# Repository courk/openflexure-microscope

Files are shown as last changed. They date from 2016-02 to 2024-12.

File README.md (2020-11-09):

# OpenFlexure Microscope
The OpenFlexure Microscope is a  3D printable microscope, including a precise mechanical stage to move the sample and focus the optics.  There are many different options for the optics, ranging from a webcam lens to a 100x, oil immersion objective.

A trio of microscopes

The trick of making a microscope out of a webcam has been around for a little while, and produces good results.  However, getting a nice mechanical stage to focus the microscope and move around on the sample is tricky.  This project is a 3D printable design that enables very fine (sub-micron) mechanical positioning of the sample and the lens, with surprisingly good mechanical stability.  It's discussed in various [media articles](https://gitlab.com/openflexure/openflexure-microscope/wikis/Media-Articles).

If you use the OpenFlexure microscope in you work please consider citing one of our papers:

* *Robotic microscopy for everyone: the OpenFlexure microscope*, [Biomedical Optics Express **11** 2447 (2020)](https://doi.org/10.1364/BOE.385729) (open access).
* *A one-piece 3D printed flexure translation stage for open-source microscopy*, [Review of Scientific Instruments **87**, 025104 (2016)](http://dx.doi.org/10.1063/1.4941068) (open access).

## Building a microscope
For up-to-date build instructions, STL files, and pre-built Raspberry Pi SD images, please head to the [build a microscope page].

[build a microscope page]: https://openflexure.org/projects/microscope/build

## Instructions
The latest release of our assembly documentation can be found from the [build a microscope page] on our website. The editable instructions are Markdown format, in the [docs folder](./docs/) of this repository. If you have a problem accessing the images after cloning the repository see the section on LFS files below.

## Printing it yourself
Configure your microscope hardware and download the STL files through the [microscope STL configurator] page.  The [assembly instructions](https://build.openflexure.org/openflexure-microscope/latest/docs) contain instructions on print settings and putting it together.

If you've built one, let us know. You can let us know on [our forum](https://openflexure.discourse.group/), add yourself to the [wiki page of builds](https://gitlab.com/openflexure/openflexure-microscope/wikis/Assembly-Logs), or submit an [issue](https://gitlab.com/openflexure/openflexure-microscope/issues/new) marked as a build report.  This is a really helpful for us even if you don't suggest improvements or flag up problems.

[microscope STL configurator]: https://microscope-stls.openflexure.org

## Come join us!
Most of the development of this design has been done as part of various [research projects](http://www.bath.ac.uk/physics/contacts/academics/richard-bowman/index.html) - if you would like to join our research group at Bath, and you have funding or are interested in applying for it, do get in touch.  Check the University of Bath jobs site, or findaphd.com, to see if we are currently advertising any vacancies.  The team is bigger than Bath, though, and there are contributors in Cambridge, Dar es Salaam, and beyond.

## Kits and License
This project is open-source and is released under the CERN open hardware license.  We are working on bring able to sell kits through [OpenFlexure Industries Ltd.](https://www.openflexure.com/), and will update here once we have a good way of doing it.

## Get Involved!
This project is open so that anyone can get involved, and you don't have to learn OpenSCAD to help (although that would be great).  Ways you can contribute include:

* [Join our forum](https://openflexure.discourse.group/)
* Get involved in [discussions on gitter] (we use this less than the forum)(https://gitter.im/OpenFlexure-Microscope/Lobby) 
* Share your microscope images (of both microscopes and what you've seen with them) on social media - you can mention @openflexure on Twitter.
* [Raise an issue on the helpdesk](https://gitlab.com/openflexure/openflexure-helpdesk/-/issues) if you spot something that's wrong, or something that could be improved.  Helpdesk issues can be about anything to do with the project including the instructions/documentation, the software, etc.
* Suggest better text or images for the instructions.
* Improve the design of parts - even if you don't use OpenSCAD, STL files or descriptions of changes are helpful.
* Fork it, and make merge requests - again, documentation improvements are every bit as useful as revised OpenSCAD files.

Things in need of attention are currently described in [issues](https://gitlab.com/openflexure/openflexure-microscope/issues/) so have a look there if you'd like to work on something but aren't sure what.

## Developing
If you want to play with the OpenSCAD files or change the documentation, you should fork the repository.  You can edit the documentation online in GitLab, or clone the repository if you want to edit the OpenSCAD files.  You will need to clone the whole repository as the OpenSCAD files are dependent on each other.

### Development environment
We mostly use VSCode to edit the OpenSCAD files, and then use OpenSCAD with the editor hidden and the "automatic reload and compile" option ticked.  This is much nicer for a big multi-file project like the microscope than relying on OpenSCAD's built-in editor, and also works nicely with version control.

You can edit ``microscope_parameters.scad`` to change which options you build in the OpenSCAD window, but it's best not to commit changes to that file unless you need to change the default values.

### Automatic builds
The build system is based on Python and Ninja, see [compiling](COMPILE.md) for more details.

### Release flow
We use GitLab CI to manage builds and deployment.

The CI will build STL files that will remain on GitLab for 1 week when:

* A merge request is submitted
* A merge request is modified

The CI will build and deploy STL files and documentation to [build.openflexure.org](https://build.openflexure.org/) when:
* A build is manually triggered from GitLab web
* A release is tagged

The build server will mark a release as "latest" ([build.openflexure.org/openflexure-microscope/latest](https://build.openflexure.org/openflexure-microscope/latest)) when a release is tagged, with a full semantic version and no suffix. For example:
  * v6.0.0 will replace "latest"

However, incomplete semantic versions will not replace latest. For example:
  * v6.0.1-beta.1 will **not** replace "latest" (pre-release suffix)
  * v6.1 will **not** replace "latest" (no patch version specified)
  * 6.0.1a will **not** replace "latest" (non-standard suffix)

### LFS files

This repository stores images using Git LFS. This means that cloning the repository without Git LFS installed will only download placeholders for the images. Follow these instructions to [install Git LFS](https://git-lfs.github.com/).

With LFS installed Git will download the latest version of the images used in the documentation. If they are still missing try running:
```
git lfs fetch
git lfs checkout
```

**Download all files**

To make Git always download *everything* in the repository run the following commands in your terminal:
```
git config --local lfs.fetchexclude ""
git lfs fetch
git lfs checkout
```

## Related Repositories

Other repositories relating to the Openflexure Microscope are in the [OpenFlexure GitLab group](https://gitlab.com/openflexure).  Particularly useful ones are:

* [OpenFlexure Microscope Server](https://gitlab.com/openflexure/openflexure-microscope-server). This is the software that runs on the microscope.
* [OpenFlexure Connect](https://gitlab.com/openflexure/openflexure-connect). The recommended client software for controlling the microscope. The repository is mostly device discovery code, with the interface handled by the server.
* [OpenFlexure Microscope Python Client](https://gitlab.com/openflexure/openflexure-microscope-pyclient). This allows you to control a microscope from a python script.
* [OpenFlexure Delta Stage](https://gitlab.com/openflexure/openflexure-delta-stage). A 3-axis stage for microscopy that keeps the objective in a fixed position.
* [OpenFlexure Block Stage](https://gitlab.com/openflexure/openflexure-block-stage). A higher precision 3-axis stage with a smaller range.

Repositories for compatible motor controllers:
* The ["sangaboard" motor controller](https://gitlab.com/bath_open_instrumentation_group/sangaboard). The standard motor controller for the microscope. Developed collaboratively with [STICLab](http://www.sticlab.co.tz)
* The ["fergboard" motor controller](https://github.com/fr293/motor_board) by Fergus Riche.

A number of other related projects include:

* [micat](https://gitlab.com/bath_open_instrumentation_group/micat) For microscope calibration
* [PiCamera CRA Compensation](https://gitlab.com/bath_open_instrumentation_group/picamera_cra_compensation/) Contains hardware and software for colour calibration of a Raspberry Pi camera.
* Some [characterisation scripts for analysing images of the USAF resolution test target](https://github.com/rwb27/usaf_analysis/)

Some open flexure repositories still remain on [Richard's Github](https://github.com/rwb27/).

## Compiling from source
If you want to print the current development version, you can compile the STL from the OpenSCAD files - but please still consult the documentation for quantities and tips on print settings, etc.  You can use Ninja build to generate all the STL files (run ``pip3 install -r requirements.txt`` and then ``./build.py`` in the root directory of the repository).  More instructions are available in [COMPILE.md](COMPILE.md).

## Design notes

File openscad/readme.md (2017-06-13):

OpenFlexure Microscope: OpenSCAD Source
=======================================

This folder contains the source code that generates the STL files that you print to produce the microscope.  The relationship between the source files and the STL files is not yet 1:1, though I'm gradually working on that.  Most of the SCAD files produce a corresponding STL, but there are a few key support files that don't:

* ``microscope_parameters.scad`` defines most of the important variables (parameters) used in the design, for example the size of the microscope, whether or not it has motor lugs, etc. etc. - this is the file you are most likely to need to modify, for example to produce a microscope with particular settings.
* ``utilities.scad`` contains lots of handy functions I've coded along the way.  It's a slightly random assortment, but they are used in most of the other files and save a fair bit of typing.
* ``dovetail.scad`` defines the dovetail clips used to hold the optics module and the condenser.
* ``compact_nut_seat.scad`` defines the actuator column (the bit that holds the screw, nut and elastic band).  This is one of the most useful files for other projects - e.g. the OpenFlexure Block Stage uses it extensively.
* ``logo.scad`` is used to stamp the WaterScope logo on the microscope

Then for the main parts of the microscope:
* ``main_body.scad`` defines the main body.  This is by far the biggest file as you might expect.
* ``feet.scad`` produces the three front feet (two tilted and one untilted)
* ``gears.scad`` makes 3 gears for the actuators.
* ``illumination_and_rear_foot.scad`` produces the illumination column, which is combined with the back foot.  It's now in three pieces, for easier printing and to allow some adjustment of the condenser position.
* ``optics.scad`` defines, amongst other things, the optics module (the mount for the camera and objective).  This has a number of commented-out sections that must be uncommented depending on what you want to produce.  In particular, you must choose manually between an RMS objective and using a simpler lens.  You must also uncomment the correct line at the top of the file for the camera - the design will work with several camera modules defined in the ``cameras`` folder.
* ``sample_clip_2.scad`` produces clips to hold microscope slides onto the microscope stage.  This is now set to print two, and produces an STL file that is print-ready (i.e. the clips are on their side).
* ``sample_riser_2.scad`` makes a 10mm thick platform for a microscope slide.  You may need to use comments at the bottom of the file to print either the sample riser or the clip that holds the slide on.  A small spring is required to put the clip in the right place.
* ``small_gear.scad`` makes the gear you fit on a motor if you want to motorise the microscope.  NB it only makes one gear.

There are some that make tools too:
* ``actuator_assembly_tools.scad`` defines the tool for inserting elastic bands, and the tooll for pushing nuts into nut slots.  NB there is a new double-ended band tool defined at the bottom of the file, you'll need to use the comments to either produce this or the old-style one.
* ``tube_lens_tool.scad`` produces a ring of plastic, suitable for pushing the tube lens into its push-fit mount without damaging it.
* ``condenser_lens_tool.scad`` produces a ring of plastic, suitable for pushing the condenser lens into its push-fit mount without damaging it.
* ``lens_removal_tools.scad`` produces the tools needed to remove the lens from the Raspberry Pi camera module.  NB the lens removal tool is now superseded by the injection-moulded tool supplied by Raspberry Pi with each camera, but the board holder still helps to avoid damaging the flex.

Other files:
* ``baseplate.scad`` and ``baseplate_minimal.scad`` generate a baseplate, suitable for gluing onto some foam, if you want to mount the microscope in a box.  It's still work in progress...
* ``illustrations/`` contains various SCAD files that aim to create the illustrations needed for the instructions.  Very much work in progress, it's nowhere near finished.

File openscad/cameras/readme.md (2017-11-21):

# OpenFlexure Microscope: Camera Mounts

Curently, the OpenFlexure microscope will work with:
* Raspberry Pi camera module v2 (v1 is possible but deprecated, as it's discontinued)
* Logitech C270 webcam (you need to dissassemble it and remove the microphone)
* USB camera with standard M12 lens (WaterScope source these from China)

The way this is done is that ``optics.scad`` includes ``camera.scad``, which defines the important functions/modules for interfacing with the camera.  These are then used to make the optics module accordingly.  The variable ``camera`` (defined in ``microscope_parameters.scad`` or on the command line). Those functions are:

* ``camera_mount_height()``: a function that returns the height of the mount (above this height, we will make the optics module - this is the distance below the ground plane of the microscope body that the camera PCB will sit).
* ``camera_sensor_height()``: the distance above the PCB that the camera sensor sits - it's used in the optics module to calculate the position of the lens.
* ``camera_mount()``: a module that builds a mount for the camera.  If you print this on its own, it should create a flat(ish) structure, ``camera_mount_height()`` high, that fits onto the camera, with the sensor centred on the origin.

There are 3 options for the camera:
* picamera_2: mount for Raspberry Pi camera v2
* logitech_c270: for Logitech C270 webcam
* m12: this replaces the M12 lens holder on a USB camera.  It should work with most cameras that have an M12 lens held onto the board by two screws.

The ``picamera_2.scad`` file also defines the cover for the bottom of the camera PCB and the tools for removing the lens (see below).  There's no cover for the Logitech PCB, I often use a bit of extra-large heatshrink (it's thinner than a printed cover would be, which is helpful).

Previous versions of the microscope had push-fit mounts for the Pi camera v1 and v2, but it was very easy to break the delicate flex on the camera module when fitting these, so they are now removed.  See previous versions if you need those.

## Pi Camera v2 accessories
The extra files ``picamera_2_<thing>.scad`` generate the board gripper and lens gripper that can be used to remove the lens of the Raspberry Pi camera v2, and a little cover for the bottom of the PCB to protect it from shorts, etc.  The lens gripper is now obsolete as a much better, injection-moulded gripper is now supplied in the pi camera box.  The gripper for the PCB is still useful as it protects the flex cable from damage while you remove the lens.

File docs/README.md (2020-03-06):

# OpenFlexure Microscope Documentation
The documentation is best viewed [on openflexure.org][built_docs].  If you have problems or want to suggest improvements, please [raise an issue] or even better edit the markdown file in this folder and send us a pull request.

The assembly instructions are contained in this folder, in MarkDown format.  They will eventually use [Git-Building] to automatically generate the bill of materials, which means the markdown files will make sense if you view them directly, but you're better off using the [processed versions][built_docs] on openflexure.org.

## Improving the documentation
If you would like to improve the documentation, the easiest way is to use the "edit" or "web IDE" features on GitLab.  Good instructions are super important, so it's really helpful to have suggestions and improvements from people who have built the microscope.  You can fork the repository and work on it locally if you prefer.  

**Please note that this repository uses [Git LFS] and that, by default, it won't download the images for the documentation** (before switching to LFS, it was a 1.5Gb download to clone the repository, which causes real problems for some of the team).  To change which files Git LFS downloads please see the instructions in the main [README](../README.md) for the repository.

## Build instructions
Currently, the process of getting the docs onto [openflexure.org][built_docs] is a bit manual; first you need to add Jekyll "front matter" to the pages and copy them into a new location.  That's done by ``build_docs.py`` (in this directory - use Python 3 or it won't work).  You can then copy all the files from the built directory (``../builds/docs/`` by default) into the relevant folder in the repoisitory for openflexure.gitlab.io, and push to master at which point the Jekyll site will be built.  We will hopefully switch to using gitbuilding in the near future to improve this and automate our bill of materials generation.  You can of course serve the output folder as a Jekyll site directly if you add a config file, but bear in mind that it might get deleted when you rebuild the output folder, so keep a copy somewhere else!  This will be fixed in the future when we are using gitbuilding.

[built_docs]: https://www.openflexure.org/projects/microscope/docs/
[Git LFS]: https://git-lfs.github.com/
[Git-Building]: https://gitlab.com/bath_open_instrumentation_group/git-building
[raise an issue]: https://gitlab.com/openflexure/openflexure-microscope/issues/new

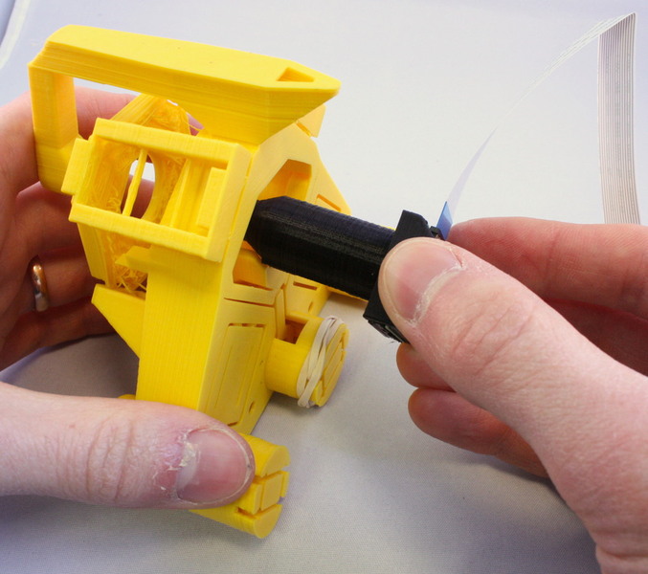
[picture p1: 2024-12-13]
docs/images/optics_insertion_1.jpg

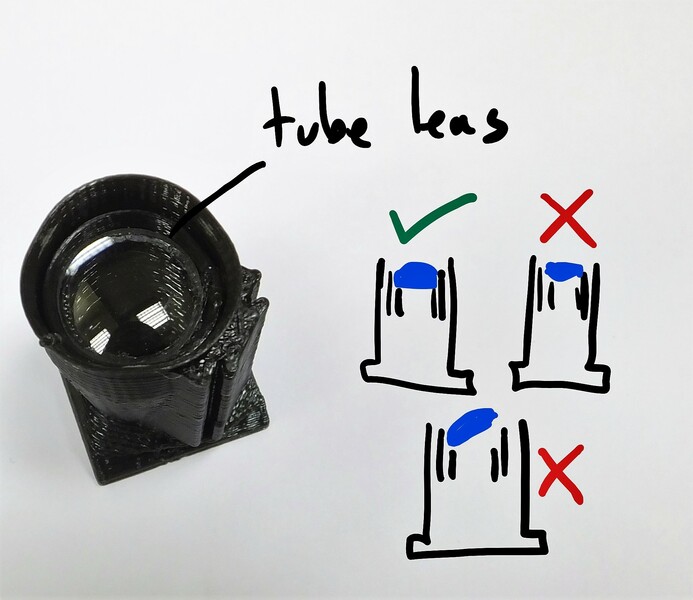
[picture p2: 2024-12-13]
docs/images/hires_optics_tubelens_2.jpg

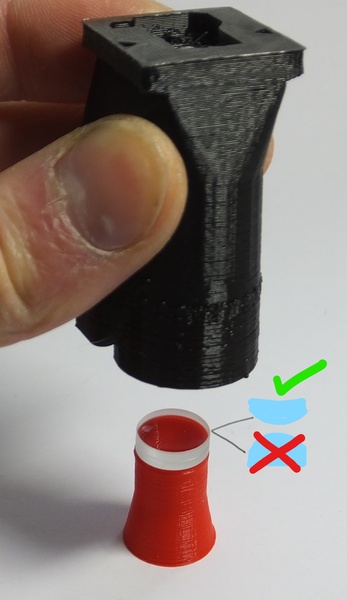
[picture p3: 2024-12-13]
docs/images/hires_optics_tube_lens_1.jpg

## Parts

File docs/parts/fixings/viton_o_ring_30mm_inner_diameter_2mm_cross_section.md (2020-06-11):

# Viton O ring, 30mm inner diameter, 2mm cross section

## Details
*   **Material:** Viton or Nitrile
*   **Inner diameter:** 30mm
*   **Cross-section:** 2mm
*   **Outer diameter:** 34mm
*   **Supplier website:** [http://www.simplybearings.co.uk/]

The O-rings function as springs, to provide a return force on the nut that is pulled upwards by the screw.  I use Viton O-rings, 30mm ID, as they provide about the right force.  You can substitute for rubber bands, but it's difficult to specify the size directly, and they tend to perish and snap in a few weeks.  Viton O rings are well worth the effort and price!

## Alternatives
If you're unable to get hold of Viton O rings of the correct size, substituting for Nitrile or EPDM is probably also fine - though most of our testing has been done with Viton.  

Rubber bands from a stationary store can work, though in our experience they usually perish after a few weeks.  Unfortunately, that happens whether or not they are used.  It's also usually quite hard to get rubber bands exactly the right size.

It's possible to print elastic bands using TPU filament, as described in Bill Schaller's contribution.  Print this part using .1mm layer height, with randomized perimeter start and end positions if possible. For strength, the part should be printed entirely with perimeters, no gap fill. The part is designed to be printed with a 0.4mm nozzle. Printing with a 1mm nozzle hasn't been tested, and isn't recommended.  The part for this is ``actuator_tension_band.stl`` and should be included in the automated build system.

It's also possible to improvise with bungee cord as described by @MisterBurnley in his [build report](https://gitlab.com/openflexure/gallery-wiki/-/issues/5#note_348619271).

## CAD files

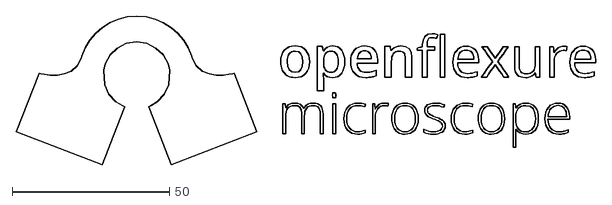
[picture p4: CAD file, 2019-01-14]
openscad/openflexure_logo.dxf
184.0 x 47.3

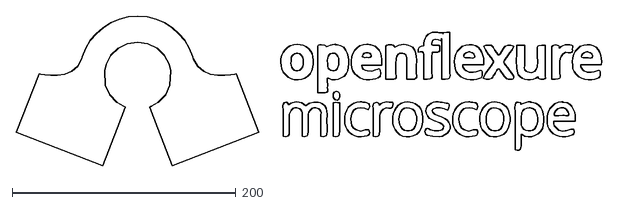
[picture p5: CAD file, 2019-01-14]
openscad/openflexure_logo_outset.dxf
524.2 x 134.0

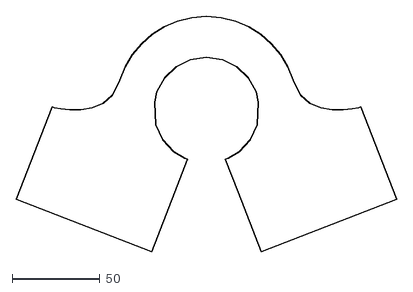
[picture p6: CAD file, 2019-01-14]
openscad/openflexure_emblem.dxf
216.7 x 134.0

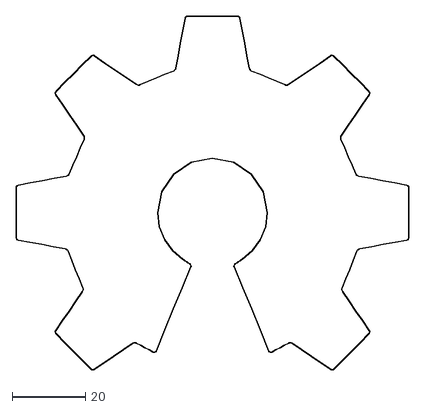
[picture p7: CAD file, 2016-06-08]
openscad/oshw_gear.dxf
107.1 x 96.4

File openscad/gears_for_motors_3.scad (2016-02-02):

use <MCAD\involute_gears.scad>;
use <utilities.scad>;

//pi=3.14159;
//$fn=32;
strut_t=3;
depth = 40;
ratio = 2;
teeth_smallgear = 12;
teeth_biggear = teeth_smallgear * ratio;
c2c_distance = 20; //see output from motor_lugs
pitch = c2c_distance * 360 / (teeth_smallgear + teeth_biggear);
d=0.05;

//pitch radius = Nteeth * circular_pitch / 360
//pitch radius is centre of gear to meshing point
//outer radius = pitch radius * (1 + 2*pi/Nteeth)
//our c2c distance is 10+12.5mm=22.5mm, 
module large_gear(){
	assign($fn=32, pi=3.14159, pitch_r=c2c_distance*(ratio/(ratio+1)))
	difference(){
		intersection(){
			gear(number_of_teeth=teeth_biggear,
				circular_pitch=pitch,
				circles=0,
				gear_thickness=6,
				hub_thickness=6,
				hub_diameter=20,
				rim_thickness=6,
				bore_diameter=1);	
			cylinder(r1=pitch_r-2,r2=pitch_r+18,h=20); //stop bottoms of teeth being funny
		}
		translate([0,0,1.5]) nut(3,shaft=true,fudge=1.2,h=999);
//		for(i=[0:5]) rotate(i*60) translate([pitch_r*0.55,0,0.5]) cylinder(r=pitch_r*0.2,h=999);
	}
}

module small_gear(){	
	$fn=32;
    pi=3.14159;
    h=8;
    flat_h=h-3.5;
    shaft_r=5/2*1.1;
    pitch_r=c2c_distance*1/(ratio+1);
	difference(){
		union(){
			gear(number_of_teeth=teeth_smallgear,
					circular_pitch=pitch,
					circles=0,
					gear_thickness=h,
					hub_thickness=h,
					hub_diameter=1,
					rim_thickness=h,
					bore_diameter=1);
				
			cylinder(r=pitch_r+pi*pitch_r/teeth_smallgear,h=0.5); //help adhesion
		}
        //cut-out for motor shaft
		intersection(){
			cylinder(r=shaft_r, h=999, center=true);
			sequential_hull(){
                translate([0,0,-d]) cube([999,3,d]*1.1,center=true);
                translate([0,0,flat_h]) cube([999,3,d]*1.1,center=true);
                translate([0,0,flat_h+2]) cube([999,7,d]*1.1,center=true);
                translate([0,0,999]) cube([999,7,d]*1.1,center=true);
            }
		}
        //chamfer the top/bottom for better fit
        translate([0,0,h]) cylinder(r1=shaft_r,r2=shaft_r+2,h=2,center=true);
        translate([0,0,0]) cylinder(r2=shaft_r,r1=shaft_r+2,h=2,center=true);
	}
}


rotate(360/teeth_biggear/2) large_gear();
//translate([c2c_distance*2,00]) small_gear();

module thumbwheel(r=10,h=5,knobble_r=1,knobble_angle=45,chamfer=0.5){
    knobble_length=knobble_r * sin(knobble_angle) * 2;
    n_knobbles = floor(2*3.141*r/knobble_length);
    difference(){
        intersection(){
            union(){
                for(i=[1:n_knobbles]) rotate(i/n_knobbles*360){
                    translate([0,r-knobble_r,0]) cylinder(r=knobble_r,h=h,$fn=16);
                }
                cylinder(r=r-knobble_r,h=h,$fn=n_knobbles);
            }
            cylinder(r1=r-knobble_r-chamfer, r2=r-knobble_r-chamfer+999,h=999,$fn=n_knobbles);
            translate([0,0,h-999])cylinder(r2=r-knobble_r, r1=r-knobble_r+999,h=999,$fn=n_knobbles);
        }
        translate([0,0,1.5]) nut(3,shaft=true,fudge=1.2,h=999);
    }
}
//thumbwheel();

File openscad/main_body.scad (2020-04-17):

/******************************************************************
*                                                                 *
* OpenFlexure Microscope: Microscope body                         *
*                                                                 *
* This is the chassis of the OpenFlexure microscope, an open      *
* microscope and 3-axis translation stage.  It gets really good   *
* precision over a ~10mm range, by using plastic flexure          *
* mechanisms.                                                     *
*                                                                 *
* (c) Richard Bowman, January 2016                                *
* Released under the CERN Open Hardware License                   *
*                                                                 *
******************************************************************/

use <./utilities.scad>;
use <./compact_nut_seat.scad>;
use <./logo.scad>;
use <./dovetail.scad>;
use <./z_axis.scad>;
use <./gears.scad>;
use <./wall.scad>;
use <./main_body_transforms.scad>;
use <./reflection_illuminator.scad>;
include <./microscope_parameters.scad>; //All the geometric variables are now in here.


module leg(brace=stage_flex_w){
    // The legs support the stage - this is either used directly
    // or via "actuator" to make the legs with levers
    fw=stage_flex_w;
	union(){
       	//leg
		reflect([1,0,0]){
			//vertical legs
			translate([leg_middle_w/2+zflex_l,0,0]) hull(){
				cube(leg);
				cube([leg[0],fw+brace,d]); //extend it to be a triangle
			}

            //flexure bridges between the legs
            zs = [flex_z1, flex_z2]; //heights of bridges between legs
            bs = [brace, 0]; //"brace positions" - a nonzero value here
                             //widens the leg, and adds another flexure
                             //at the new position.  bs[i]=fw will double
                             //the width of the flexure, while a larger 
                             //value produces two distinct flexures.
			for(i=[0,1]) translate([0,0,zs[i]]){
				translate([-d,0,0]) hull() repeat([0,bs[i],0],2) //solid part
                        cube([leg_middle_w/2+d,leg[1],stage_t-0.2*leg[1]]);
				translate([-d,0,0]) repeat([0,bs[i],0],2) //flexures
                        cube([leg_middle_w/2+zflex_l+leg[0],leg[1],zflex_t]);
			}
		}
        
		//thin links between legs
		if(flex_z2-flex_z1 > 2*bridge_dz){
			n=floor((flex_z2-flex_z1)/bridge_dz);
			dz=(flex_z2-flex_z1)/n;
			translate([0,leg[1]/2,flex_z1+dz]) repeat([0,0,dz],n-1) cube([leg_outer_w,2,0.5],center=true);
		}
	}
}
module actuator(){
    // A leg that supports the stage, plus a lever to tilt it.
    // No longer includes the flexible nut seat actuating column.
    // TODO: find the code that unifies this with leg()
	brace=20;
    fw=stage_flex_w;
    w = actuator[0];
    union(){
        leg(brace=brace);

		//arm (horizontal bit)
		difference(){
            sequential_hull(){
                translate([-leg_middle_w/2,0,0]) cube([leg_middle_w,brace+fw,4]);
                translate([-w/2,0,0]) cube([w,brace+fw+0,actuator[2]]);
                translate([-w/2,0,0]) cube(actuator);
            }
            //don't foul the actuator column
            translate([0,actuating_nut_r,0]) actuator_end_cutout(); 
        }

	}
}
module actuator_silhouette(h=999){
    // This defines the cut-out from the base structure for the XY
    // actuators.
    linear_extrude(2*h,center=true) minkowski(){
        circle(r=zflex_l,$fn=12);
        projection() actuator();
    }
}

module back_foot_mounting_screw(d=3*0.95, h=16, center=true){
    translate([0,illumination_clip_y+3,0]) cylinder(d=d, h=h,center=center);
}

module mounting_hole_lugs(){
    // lugs either side of the XY table to bolt the microscope down
    //these are to mount onto the baseplate 
    for(p=base_mounting_holes) {
        if(p[1]<0 && p[0]>0) reflect([1,0,0]) hull(){
            translate([z_flexure_x,0,0]) rotate(-120) cube([10,d,10]);
            translate(p) cylinder(r=4*1.1,h=3);
        }
    }
}

module xy_limit_switch_mount(d=3.3*2, h=6){
    // A mount for the XY limit switch (M3)
    leg_frame(45) translate([-9, -zflex_l-zawall_h*sin(6)-3.3+1, zawall_h-6]) cylinder(d=d,h=h);
}


// The "wall" that forms most of the microscope's structure
module wall_inside_xy_stage(beamsplitter=false){
    front_wall_height = beamsplitter ? zawall_h : wall_h;
    // First, go around the inside of the legs, under the stage.
    // This starts at the Z nut seat.  I've split it into two
    // blocks, because the shape is not convex so the base
    // would be bigger than the walls otherwise.
    reflect([1,0,0]) sequential_hull(){
        //inner_wall_vertex(-45, -leg_outer_w/2-wall_t/2, zbwall_h);
        mirror([1,0,0]) z_bridge_wall_vertex();
        z_bridge_wall_vertex();
        inner_wall_vertex(45, -leg_outer_w/2, zawall_h);
        z_anchor_wall_vertex();
        inner_wall_vertex(135, leg_outer_w/2, zawall_h);
        inner_wall_vertex(135, -leg_outer_w/2, front_wall_height);
        inner_wall_vertex(-135, leg_outer_w/2, front_wall_height);
    };    

}

module wall_outside_xy_actuators(){
    // Add the wall from the XY actuator column to the middle
    sequential_hull(){
        z_anchor_wall_vertex(); // join at the Z anchor 
        // [nb this is no longer actually the z anchor since the new z axis]
        // anchor at the same angle on the actuator
        // NB the base of the wall is outside the
        // base of the screw seat
        leg_frame(45) translate([-ss_outer()[0]/2+wall_t/2,actuating_nut_r,0]){
            rotate(-45) wall_vertex(y_tilt=atan(wall_t/zawall_h));
        }
    }
}

module wall_inside_xy_actuators(){
    // Connect the Z anchor to the XY actuators
    hull(){
        translate([-(z_anchor_w/2+wall_t/2+1), z_anchor_y + 1, 0]) 
                     wall_vertex();
        y_actuator_wall_vertex();
    }
}

module wall_between_actuators(){
    // link the actuators together
    hull(){
        y_actuator_wall_vertex();
        translate([0,z_nut_y+ss_outer()[1]/2-wall_t/2,0]) wall_vertex();
    }
}

// Cut out hole for reflection illuminator
module fl_cube_cutout(){
    // size of cutout for fl cube
    top_cutout_w = 17.8; // As big as we can get at height 'wall_h' without bridging a corner
    mid_cutout_w = illuminator_width() + 1;
    bottom_cutout_w = illuminator_width() + 4;

    // Create a trapezoid with min width (cube_width) at top
    hull() {
        translate([-(bottom_cutout_w)/2, -49, -0.5]) cube([bottom_cutout_w, 49, 1]);
        translate([-(mid_cutout_w)/2, -49, 10]) cube([mid_cutout_w, 49, 1]); // Highest we usually need
        translate([-top_cutout_w/2, -49, wall_h]) cube([top_cutout_w, 49, 1]);
    }
}

///////////////////// MAIN STRUCTURE STARTS HERE ///////////////
module main_body(){
    // This module represents the main body of the microscope, including the positioning mechanism.

	//legs (incl. actuators)
	reflect([1,0,0]) leg_frame(135) leg();
	each_actuator(){
        actuator();
		translate([0,actuating_nut_r,0]) actuator_column(h=actuator_h, join_to_casing=true);
    }
	//flexures connecting bottoms of legs to centre
	each_leg() reflect([1,0,0]) translate([0,0,flex_z1]){
        w=stage_flex_w;
        translate([leg_middle_w/2-w,0,0.5]) hull()
			repeat([1,-1,0]*(zflex_l+wall_t/2),2) cube([w,d,zflex_t]);
    }
    //tie the legs to the wall (built later) during printing
    reflect([1,0,0]) leg_frame(135) reflect([1,0,0]) {
        translate([leg_middle_w/2+zflex[1]+zflex[0]/2, -wall_h*0.7*tan(6)-1-zflex[1], wall_h*0.7]) cube([1, wall_h*0.7*tan(6)+2+zflex[1], 0.5]);
    }

	// flexures between legs and stage
    // NB these connect the legs together, and pass all the way under the stage.  This
    // is important, if they get cut then the bridges will fail!
	difference(){
		hull() each_leg() translate([0,0,flex_z2+zflex_t/2+0.5]) cube([leg_middle_w,d,zflex_t],center=true);
		hull() each_leg() cube([leg_middle_w-2*stage_flex_w,d,999],center=true);
	}
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

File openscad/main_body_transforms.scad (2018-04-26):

/******************************************************************
*                                                                 *
* OpenFlexure Microscope: Microscope body transforms              *
*                                                                 *
* Various transforms used in the microscope.                      *
*                                                                 *
* (c) Richard Bowman, January 2016                                *
* Released under the CERN Open Hardware License                   *
*                                                                 *
******************************************************************/

use <./utilities.scad>;
use <./compact_nut_seat.scad>;
include <./microscope_parameters.scad>;

module shear_x(amount=1){
    // Shear transformation: tilt the Y axis towards the X axis
    // e.g. if amount=1, then a straight line in Y will be
    // tilted to 45 degrees between X and Y, while X lines are
    // unchanged.  This is used in the Z axis.
	multmatrix([[1,amount,0,0],
					 [0,1,0,0],
					 [0,0,1,0],
					 [0,0,0,1]]) children();
}


module leg_frame(angle){
    // Transform into the frame of one of the legs of the stage
	rotate(angle) translate([0,leg_r,]) children();
}
module each_leg(){
    // Repeat for each of the legs of the stage
	for(angle=[45,135,-135,-45]) leg_frame(angle) children();
}
module each_actuator(){
    // Repeat this for both of the actuated legs (the ones with levers)
	reflect([1,0,0]) leg_frame(45) children();
}

module place_on_wall(){
    //this is a complicated transformation!  The wall runs from
    wall_start = [z_flexure_x+wall_t/2,-wall_t/2,0]; // to
    wall_end = ([1,1,0]*(leg_r+actuating_nut_r)
                 +[1,-1,0]*(ss_outer()[0]/2-wall_t/2))/sqrt(2);
    wall_disp = wall_end - wall_start; // vector along the wall base
    // pivot about the starting corner of the wall so X is along it
    translate(wall_start) rotate(atan(wall_disp[1]/wall_disp[0]))
    // move out to the surface (the above are centres of cylinders)
    // and then align y with the vertical axis of the wall
    translate([0,-wall_t/2,0]) rotate([90-atan(wall_t/zawall_h/sqrt(2)),0,0])
    // now X and Y are in the plane of the wall, and z=0 is its surface.
    children();
}

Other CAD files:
openscad/microscope_parameters.scad
openscad/LED_array_holder.scad
openscad/accessories/1_inch_disc_holder.scad
openscad/accessories/bottom_of_main_body.scad
openscad/accessories/footprint.scad
openscad/accessories/footprint_pocket.scad
openscad/accessories/footprint_with_holes.scad
openscad/actuator_assembly_tools.scad
openscad/actuator_drilling_jig.scad
openscad/actuator_tension_band.scad
openscad/back_foot.scad
openscad/camera_mount_fl_2.scad
openscad/camera_platform.scad
openscad/cameras/6led.scad
openscad/cameras/C270_mount.scad
openscad/cameras/camera.scad
openscad/cameras/logitech_C270.scad
openscad/cameras/logitech_c270.scad
openscad/cameras/m12.scad
openscad/cameras/picam_2_push_fit.scad
openscad/cameras/picamera_2.scad
openscad/cameras/picamera_2_cover.scad
openscad/cameras/picamera_2_gripper.scad
openscad/cameras/picamera_2_lens_gripper.scad
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

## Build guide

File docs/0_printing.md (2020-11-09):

# Printing the plastic parts

First, you will need to print or obtain the 3D printed parts.  These have been designed with some care to print reliably on most RepRap-style printers, using regular PLA filament without support material.  It's important to read through the notes before, as there are multiple versions of the STL files to choose from, so it's not a good idea just to pick all the parts in the folder.  The printed parts are described in their own pages, with details of how to pick the version of that part, for the parts with multiple versions.

The best way to obtain these files is from the [microscope STL configurator] page.

[microscope STL configurator]: https://microscope-stls.openflexure.org

## Standard builds of the microscope

If you just want to build a standard version of the microscope please check print the files in the sections "Webcam-based microscope" or "High resolution microscope". A more extensive list of all available parts is at the bottom of this page if you are customising the microscope.

### Webcam-based microscope

The basic version of the microscope uses a webcam lens instead of a microscope objective - you still get a really nice focusing/sample translation stage, but with basic options.  This version is great for school or hobby use, gets a resolution of about 2um or better, and is the cheapest to build.  This is the version we usually build at workshops.  For each microscope, you will need to print one copy of each of the following files:

**Plastic tools:**

* [band and nut insertion tools, with band tool holder](./parts/printed_tools/actuator_assembly_tools.md) ``actuator_assembly_tools.stl``
* [optional] ``picamera_2_lens_gripper.stl`` (only needed if your camera didn't come with a tool to remove the lens)

**Components:**

* [body of the microscope](./parts/printed/main_body.md): ``main_body_LS65-M.stl`` or ``main_body_LS65-M_brim.stl``.
* 3 [feet](./parts/printed/feet.md): ``feet.stl`` or ``feet_tall.stl`` (contains all 3)
* 3 [large gears](./parts/printed/gears.md): ``gears.stl`` (contains all 3)
* illumination:
  * [vertical dovetail](./parts/printed/illumination_dovetail.md): ``illumination_dovetail.stl``
  * [condenser arm](./parts/printed/condenser.md): ``condenser.stl``
* 2 [sample clips](./parts/printed/sample_clips.md): ``sample_clips.stl`` (contains both)
* platform-style optics module (two parts, best with webcam lenses):
  * [camera platform](./parts/printed/camera_platform.md): ``camera_platform_<camera>_<stage size><height>.stl``
  * [lens spacer](./parts/printed/lens_spacer.md): ``lens_spacer_<camera>_<lens>_<stage_size><height>.stl`` - **Print this in black!**
* [microscope stand](./parts/printed/microscope_stand.md) or back foot
  * ``microscope_stand_no_pi_.stl`` or ``microscope_stand-30.stl`` (holds Raspberry Pi) or ``back_foot.stl``

This will need the nuts, bolts, etc. described on [the bill of materials page](./0_bill_of_materials.md), plus a camera module (for example a Raspberry Pi camera), and an option Raspberry Pi.  No other optical bits are required, except an LED for illumination.

If you want to mount a Raspberry Pi underneath the microscope (our preferred option), print ``microscope_stand.stl`` instead.  If your Raspberry Pi is in a case already, you should print ``back_foot.stl`` so the microscope sits flat on a table.  Newer Raspberry Pi camera modules include a white circular tool for unscrewing the lens.  If you don't have one, you will need to print the lens gripper (marked as optional).

### High resolution microscope

The version of the microscope used for scientific or medical research generally requires a conventional objective lens.  Most of the parts are the same, but the optics and sample mount are different.  You will need one copy of each of the following files:

**Plastic tools:**

* [band and nut insertion tools, with band tool holder](./parts/printed_tools/actuator_assembly_tools.md) ``actuator_assembly_tools.stl``
* [tool to insert](./parts/printed_tools/lens_tool.md) the 13mm diameter condenser lens and/or tube lens: ``lens_tool.stl``
* [optional] ``picamera_2_lens_gripper.stl`` (only needed if your camera didn't come with a tool to remove the lens)

**Components:**

* [body of the microscope](./parts/printed/main_body.md) (beamsplitter-compatible): ``main_body_LS65-M-BS.stl`` or ``main_body_LS65-M-BS_brim.stl``.
* 3 [feet](./parts/printed/feet.md): ``feet.stl`` or ``feet_tall.stl`` (contains all 3)
* 3 [large gears](./parts/printed/gears.md): ``gears.stl`` (contains all 3)
* illumination:
  * [vertical dovetail](./parts/printed/illumination_dovetail.md): ``illumination_dovetail.stl``
  * [condenser arm](./parts/printed/condenser.md): ``condenser.stl``
* 2 [sample clips](./parts/printed/sample_clips.md): ``sample_clips.stl`` (contains both)
* [optics module](./parts/printed/optics_module_casing.md):
  * ``optics_picamera_2_rms_f50d13.stl`` (transmission illumination) **Print this in black!**
  * ``optics_picamera_2_rms_f50d13_beamsplitter.stl`` (reflection illumination) **Print this in black!**
* [microscope stand](./parts/printed/microscope_stand.md): ``microscope_stand-30.stl`` or ``microscope_stand-30-BS.stl`` (supports reflection illumination)
* [riser for the sample](./parts/printed/sample_riser.md):  ``sample_riser_LS10.stl`` (assuming you have a microscope objective with a 45mm parfocal distance)

**For motorised operation you will also need:**

* 3 [small gears](./parts/printed/small_gears.md) for motors: ``small_gears.stl`` (contains all 3)
* [base to hold the motor driver](./parts/printed/motor_driver_case.md) (fits under the base that holds the Pi): ``motor_driver_case.stl``

**For reflection illumination you will also need:**

* [filter cube](./parts/printed/fl_cube.md): ``fl_cube.stl``
* [reflection illuminator](./parts/printed/reflection_illuminator.md): ``reflection_illuminator.stl``

**Additionally, you will need:**

* an RMS threaded, finite-conjugates [objective lens](parts/optics/objective.md).  These can be obtained from e.g. AliExpress.  Depending on whether it is 35mm or 45mm from the "shoulder" of the lens to the sample, you may or may not need the sample riser.  We almost always use 45mm "plan" corrected lenses, which do require the riser.
* a 12.7mm diameter, 50mm focal length [achromatic lens](parts/optics/tube_lens.md), e.g. ThorLabs ac127-050-a or generic equivalent.
* a 13mm diameter, 5mm focal length PMMA plano convex lens for the [condenser lens](parts/optics/condenser_lens.md) (sold as LED lenses in bulk)
* [motors](./parts/electronics/stepper_motors.md) and [motor driver electronics](6_motor_controllers.md)

## Print settings

I usually print using PLA filament with a layer size of 0.2mm, on either a Prusa i3 MK3 or an Ultimaker 2+, which takes 10 hours for the main body.  "low" quality on an Ultimaker 2 (0.15mm layers) produces similar results in about 12 hours.  Sometimes we use 0.3mm layers if we want to go even faster (8 hours or less) on our Prusa - this is unreliable on the Ultimaker.  You should be able to use pretty much any fused filament fabrication printer (i.e. any of the printers that use PLA filament).

> **Warning:** The microscope is designed to print without support material.  If you use support material it will require a lot of cleaning up, and you may well damage the parts.

The main body is designed to print without support material or adhesion layer.  If you do use an adhesion layer, many of the moving parts can be rendered useless by a brim on the main body.  It's possible to remove the brim with a craft knife, but it's very easy to damage the mechanism while doing so.  See below for our "smart brim" which should stick better to the print bed, while also being easier to remove.  This brim does a better job of not fouling the mechanism than most slicers, and is a good option if the part won't stick without a brim - see the next section.  Most of the other parts are possible to clean up after printing with a brim, so you may wish to use one, particularly for the smaller parts like sample clips.

  There are no cantilevered parts that really need support, but there are a few bridges; it might be a good idea to print the ``just_leg_test.stl`` file first, to make sure your printer can print them.  Using support material is likely to be a problem, as it will end up in places where it's hard to remove, and you are very likely to damage the mechanism while removing it.

If your printer has a standard-sized bed (180mmx180mm should be fine) then it should be possible to print the complete microscope in one go, with the exception of the bases that hold the electronics.  I do this if I'm using a machine that is well calibrated and reliable.  However, I find that it's often more reliable to print in batches (as small parts at the edge of the print bed can detach and cause it to fail).  If I need to use a brim, we generally print the main body separately using the "smart brim" and the other small parts in a separate run.  I would recommend:

There is a test file that prints a single leg of the microscope - ``just_leg_test.stl``. It's worth printing this first to check your settings are OK.

The optics module needs to print with some fine detail, so the dovetail meshes nicely with the stage.  A good way to ensure this is to print it at the same time as other parts - either print more than one optics module at a time, or print it at the same time as the microscope body.  This slows down the time for each layer, and means the plastic can cool more completely before the layer on top is deposited, resulting in a higher-quality part.  The optics module is best printed in black to cut down on stray light inside the tube - though it will still work in other colours.

## Smart Brim

For the majority of printed parts, your printer's slicer program will be able to automatically add a suitable brim to the print to improve adhesion. The exception to this is the main body, where an automatic brim is likely to fill gaps required for the movement of the sample.

This smart brim automatically determines areas suitable for a brim to be added, and adds the brim to the STL file. As the brim is part of the STL it isn't always easy to remove. Rather than simply extending the lowest layer, the smart brim edge is a seperate part printed parallel to the edge of the part being printed, making clean up significantly easier.

Sometimes slicers automatically combine the brim and the part. You can check this hasn't happened in your slicer software after slicing by previewing the lowest layer; the edges of the smart brim should appear parallel as shown below (edges of the part and brim are shown in orange).

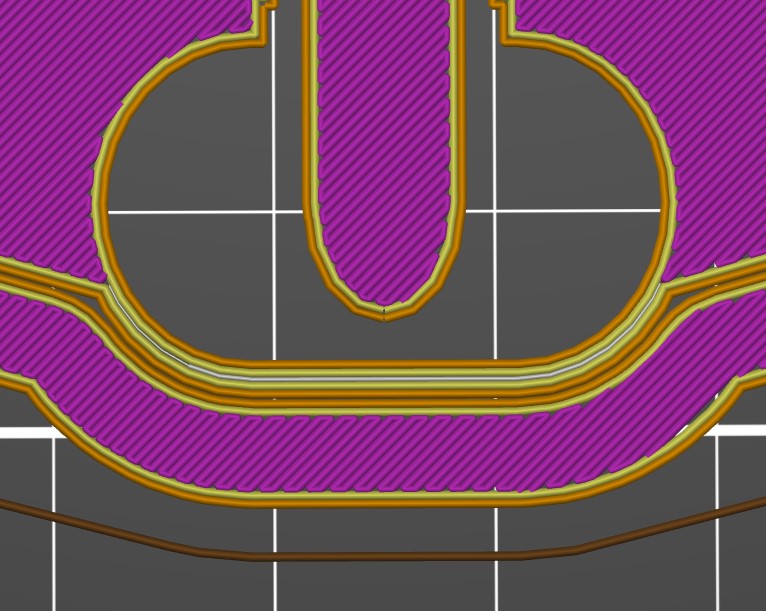
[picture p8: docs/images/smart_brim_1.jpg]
The edges of the smart brim parallel to the edge of the printed part


Regardless of your printer, when printing the microscope do not attempt to add a further brim in the slicer. Some example slicer settings required for a smart brim in different slicers are listed below.

*   **Ultimaker Cura**

Cura (v4.4) automatically slices the smarter brim suitably for printing.

*   **PrusaSlicer**

As shown below, without changing the default settings in PrusaSlicer (v2.1.1), the smart brim would be printed as an extension of the microscope base.

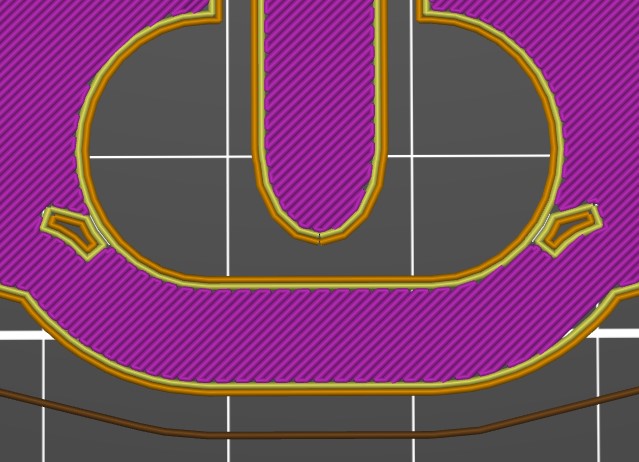
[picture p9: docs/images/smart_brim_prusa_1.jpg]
The smart brim being incorrectly printed as a solid extension of the base


This can be corrected in the "Expert" tab of PrusaSlicer. Right click on the part(s) requiring a smart brim, and open the Add settings > Advanced menu. Check the "Slice gap closing radius" box and click OK.

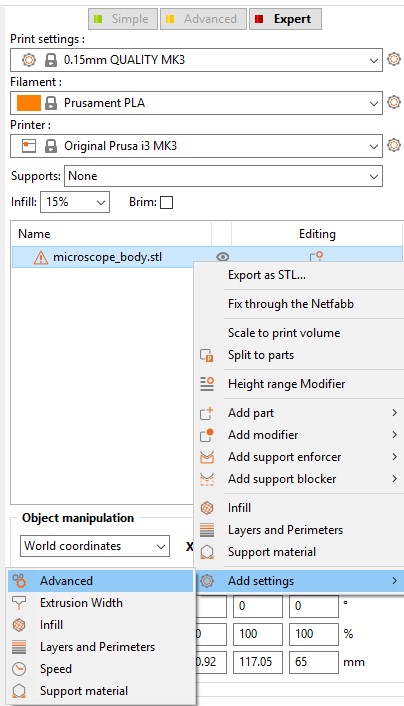
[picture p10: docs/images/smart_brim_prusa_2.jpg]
How to open the advanced settings menu


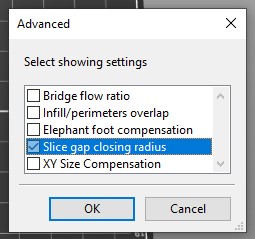
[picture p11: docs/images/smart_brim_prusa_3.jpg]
The setting to be changed


This will open a slice gap closing radius option, which should be set to 0.001 mm. This will add the option to re-slice the model, which will now print the brim as required.

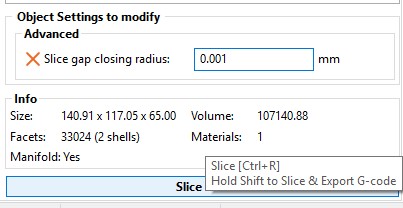
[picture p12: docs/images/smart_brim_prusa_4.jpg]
Once changing the closing radius, slice the model again as shown


The brim now printing correctly after changing Prusa settings

## Clean-up of printed parts
If you printed the parts yourself, start by opening out the three holes in the microscope body with a drill as shown.  Make sure to go all the way through.  If you don't have a drill, you can improvise by screwing in an M3 screw all the way, then forcibly rotating it with a screwdriver or the supplied nut.  Also, remove any loose strings of plastic from the underside of the sample stage, using a pair of pliers. The last step shouldn't be necessary if your machine is calibrated nicely for printing bridges.

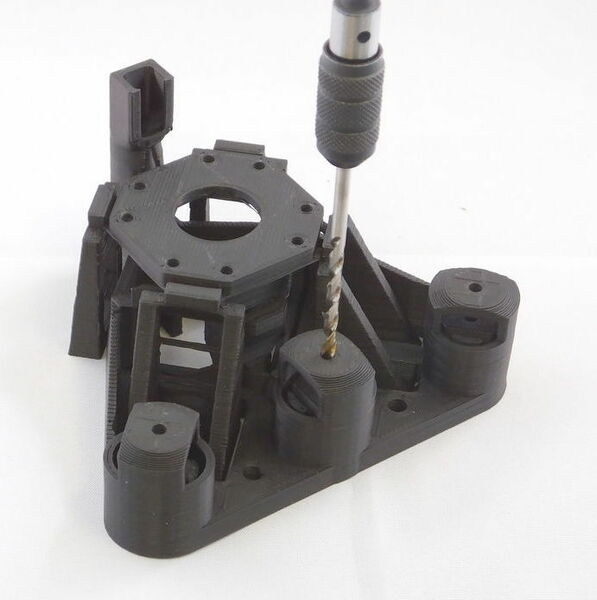
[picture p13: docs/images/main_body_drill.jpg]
Opening out the holes for the actuators


There are also ties between the actuator column casing and the central actuator column that holds the brass nut - these need to be snapped, as described in the instructions later on.  There may also be short ties between the two thinner pairs of legs and the "wall" running around the microscope - these should also be snapped with a knife.  The "ladder" like structure between each pair of legs is also only there for support during printing - it does no harm to leave it in place, but if you cut the "rungs" out, it will allow the stage to move a little more freely.

Once you have your printed parts, you can start by [assembling the actuators](./1_actuator_assembly.md).

## Extra details for custom microscopes

You can safely ignore this section if you are building one of the two standard builds listed above. If you are building a customized versions and need to understand all of your options, read on.

**Plastic tools:**
* [band and nut insertion tools, with band tool holder](./parts/printed_tools/actuator_assembly_tools.md) ``actuator_assembly_tools.stl``
* [tool to insert](./parts/printed_tools/lens_tool.md) the 13mm diameter condenser lens and/or tube lens: ``lens_tool.stl``
* [jig to hold the camera board](./parts/printed_tools/picamera_2_tools.md) while you unscrew the lens ``picamera_2_gripper.stl``
* [optional] [tool to unscrew the camera's lens](./parts/printed_tools/picamera_2_tools.md) (only needed if your camera didn't come with one) ``picamera_2_lens_gripper.stl``

**Components:**
* [body of the microscope](./parts/printed/main_body.md): ``main_body_<stage size><height>[-M].stl``.
* 3 [feet](./parts/printed/feet.md): ``feet.stl`` or ``feet_tall.stl`` (contains all 3)
* 3 [large gears](./parts/printed/gears.md): ``gears.stl`` (contains all 3)
* illumination:
 - [vertical dovetail](./parts/printed/illumination_dovetail.md): ``illumination_dovetail.stl``
 - [condenser arm](./parts/printed/condenser.md): ``condenser.stl``
* 2 [sample clips](./parts/printed/sample_clips.md): ``sample_clips.stl`` (contains both)
* optics module (you need one of the two options below):
 - old-style [optics module](./parts/printed/optics_module_casing.md) (one part, best with RMS objectives): ``optics_<camera>_<lens>_<stage size><height>.stl``
 - platform-style optics module (two parts, best with webcam lenses):
  * [camera platform](./parts/printed/camera_platform.md): ``camera_platform_<camera>_<stage size><height>.stl``
  * [lens spacer](./parts/printed/lens_spacer.md): ``lens_spacer_<camera>_<lens>_<stage_size><height>.stl``
* [optional] camera cover: ``picamera_2_cover.stl``
* [optional] 3 [small gears](./parts/printed/small_gears.md) for motors: ``small_gears.stl`` (contains all 3)
* [optional] [riser for the sample](./parts/printed/sample_riser.md): ``sample_riser_<stage size><thickness>.stl``
* [optional] slide holder that works better if using immersion oil: ``slide_riser_LS10.stl``
* [optional] [base to hold a Raspberry Pi](./parts/printed/microscope_stand.md): ``microscope_stand.stl``
* [optional] [base to hold the motor driver](./parts/printed/motor_driver_case.md) (fits under the base that holds the Pi): ``motor_driver_case.stl``
* [optional] [back foot](./parts/printed/back_foot.md), in case you are not using the microscope stand: ``back_foot.stl``

In the filenames above, where there are multiple versions, parameters are included in angle brackets:
* ``<stage size>`` selects the size of the platform - but currently only ``LS`` is supported.
* ``<height>`` is the height from the bottom of the main body to the top of the stage in mm, currently either ``65`` or ``75``.
* Usually the above two parameters occur next to each other, so you will see ``LS65``.  I pretty much only use ``65`` as standard, and if I am using an objective (which is the norm) I add a 10mm riser.
* ``<camera>`` is the camera you are using, either ``picamera_2`` for the Raspberry Pi camera module v2, ``c270`` for the Logitech C270, or ``m12`` for a camera with a screw-on M12 lens mount.
* ``<lens>`` is the lens you are using, either ``pilens``, ``c270_lens``, or ``m12_lens`` if you are using the lens that came with your camera.  To use a finite-conjugate, RMS threaded objective lens, you should specify ``rms_f50d13`` (for a 50mm focal length, 12.7mm diameter tube lens, e.g. ThorLabs ac127-050-a).  You can also specify ``rms_f40d16`` (to use a Comar tube lens, focal length 40mm, diameter 16mm) but this is deprecated as the images weren't as good.
* ``<thickness>`` is the thickness of a stage riser - the amount it adds to the height.  Usually a 10mm riser is used with a 65mm body to allow a 45mm parfocal distance objective to be used, currently only LS10 is reccommended.
Optional bits of filenames are in square brackets above:
* ``-M`` in the body name means it has motor lugs to allow 28BYJ-48 stepper motors to be fitted
* ``_tall`` on the illumination or the feet means the body sits 26mm off the ground rather than 15mm, to give clearance for larger camera modules.  This is only useful if you are not using the microscope stand.

Currently, there are two reccommended versions of the body; ``LS65`` and ``LS65-M``.  The only difference is that the ``-M`` version can be fitted with motors.  To build the high-resolution version of the microscope, use the 10mm thick sample riser ``sample_riser_LS10.stl``, and ``optics_picamera_2_rms_f50d13_LS65.stl``.  To build the low-resolution version, don't use the sample riser, and instead use ``camera_platform_picamera_2_LS65.stl`` and ``lens_spacer_picamera_2_pilens_LS65.stl``.  In both cases, it's best to print the microscope stand, and use the standard-height feet.

**Printable elastic bands**
If you are not able to get hold of Viton O rings, one possible alternative is to print some O rings using flexible TPU filament.  The STL file to use for this is ``actuator_tension_band.stl``.  More details are given in the [part page for O rings](./parts/fixings/viton_o_ring_30mm_inner_diameter_2mm_cross_section.md).

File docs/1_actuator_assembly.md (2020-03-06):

# Actuator assembly
There is one "actuator column" for each of the three axes of the OpenFlexure Microscope stage, to allow you to move the sample in X and Y, or focus the microscope by moving in Z.  It consists of a plastic gear that fits onto an M3 screw, which then pulls up on a brass nut.  Elastic bands pull down on the nut, tensioning the system.  The elastic band tightens up the mechanism, allowing us to move up and down smoothly.  Without the elastic band, you will only be able to move in one half of the microscope's range of travel, and the mechanism will be more wobbly.

# Requirements
All the parts you need for this step are in the picture below:

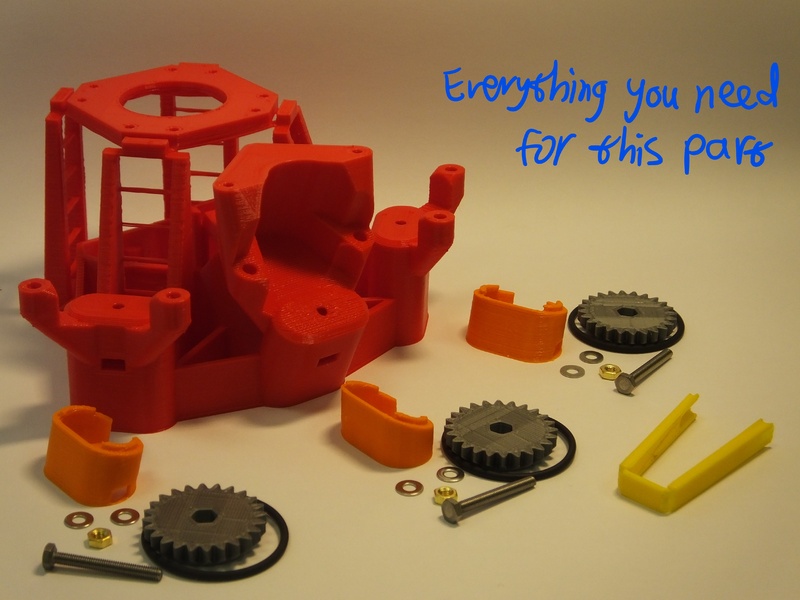
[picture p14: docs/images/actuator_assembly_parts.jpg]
Parts required for this step


## Parts
*   3x [M3x25mm hexagon head screws](./parts/fixings/m3x25mm_hexagonhead_screw.md), stainless steel
*   3x [M3 brass nut](./parts/fixings/m3_brass_nut.md)
*   6x [M3 stainless steel washers](./parts/fixings/m3_washer.md)
*   3x [Viton O-ring, 30x2mm](./parts/fixings/viton_o_ring_30mm_inner_diameter_2mm_cross_section.md) (NB: get some spares!)
*   3 [Plastic gears](./parts/printed/gears.md)
*   1 set of [Microscope Feet](./parts/printed/feet.md) (NB there are different feet for X/Y axes and for the Z axis).
*   light grease (if available)

## Tools
*   [Nut and O ring insertion tools](./parts/printed_tools/actuator_assembly_tools.md)
*   Craft knife

# Assembly Instructions
There are three actuator columns on the microscope, for X, Y, and Z.  Follow these instructions for each column in turn.

## Step 1
We need to place a nut inside the actuator.  Insert it from the side, through the slot in the actuator column, and push it into place with the [nut insertion tool](./parts/printed_tools/actuator_assembly_tools.md).  Take care to insert the nut corner-first (i.e. with flat sides parallel to the tool), otherwise it will jam.

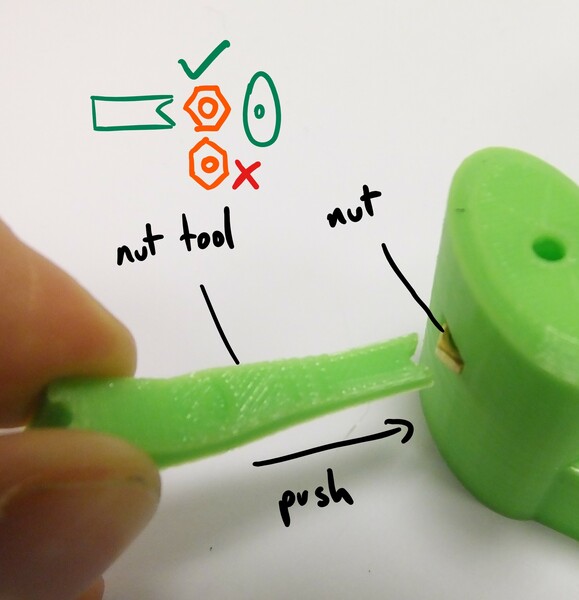
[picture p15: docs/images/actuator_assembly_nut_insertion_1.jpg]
putting the nut into the actuator column

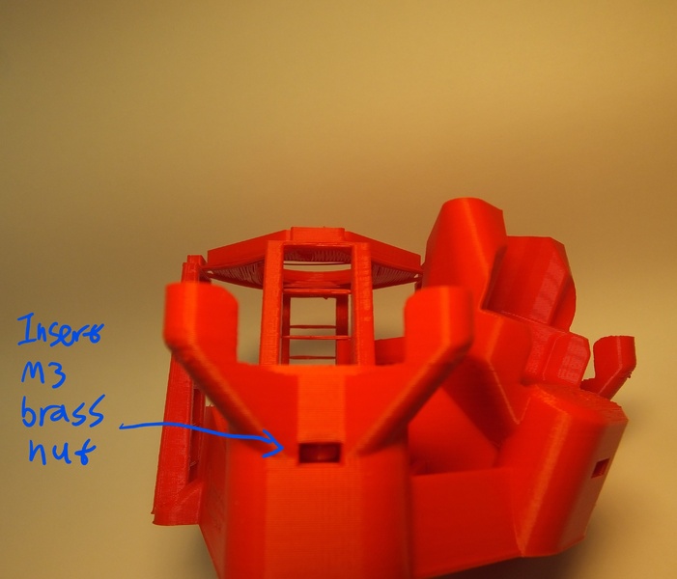
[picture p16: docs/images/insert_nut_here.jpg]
The slot in the body now looks like this


## Step 2
Next, take a screw, and push it into a plastic gear, so that the head of the screw is embedded in the plastic.  Then, thread two washers onto the screw where it sticks out of the gear.  Put a very small blob of light oil or grease (if available) on the screw thread.  Put the screw into the hole at the top of the column, and screw it into the nut that is now inside the actuator.  The two washers should sit between the gear and the microscope body

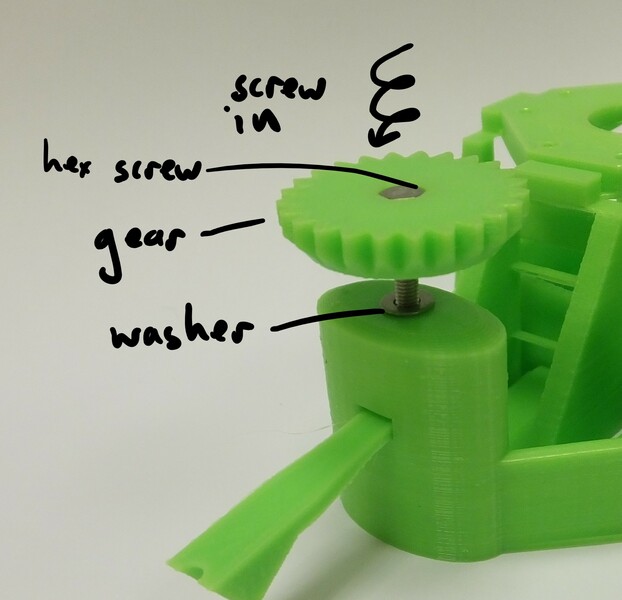
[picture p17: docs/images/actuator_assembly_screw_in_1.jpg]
assembling the screw into the actuator column

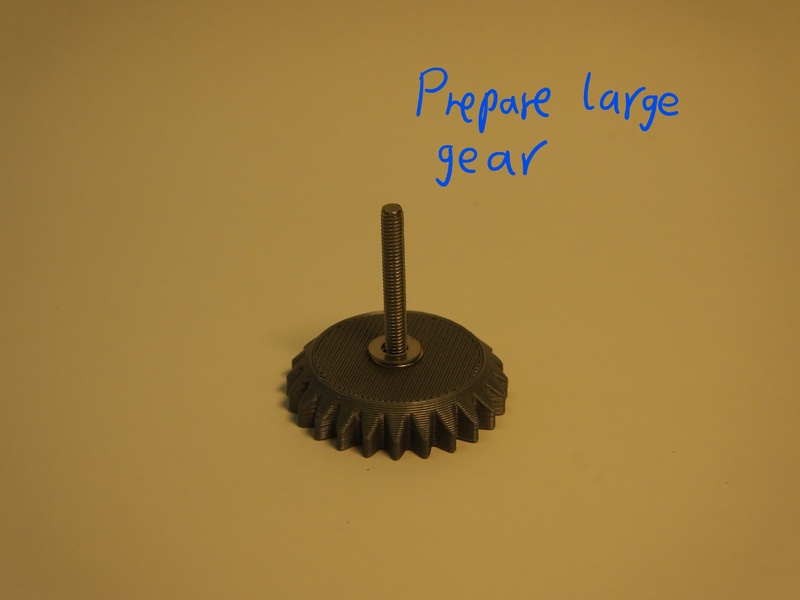
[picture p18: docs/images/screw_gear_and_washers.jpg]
The gear, with the screw and washers in place


## Step 3
Turn the microscope over and, using the elastic band tool or a craft knife, snap the two thin plastic supports as shown if they are present.
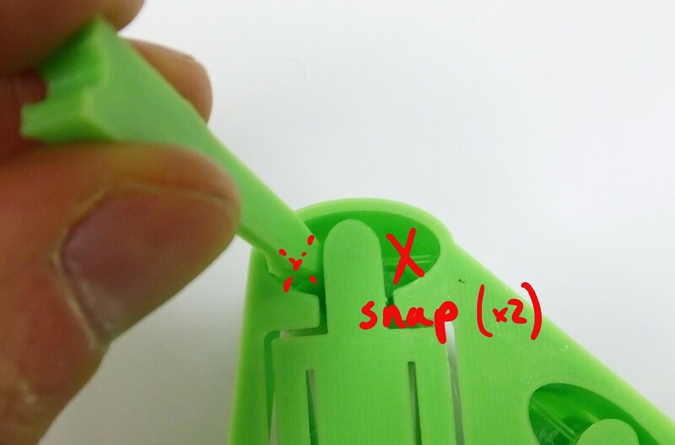
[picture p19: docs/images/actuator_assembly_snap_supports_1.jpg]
removing the ties that support the actuator column during printing


## Step 4
Hook one of the Viton bands over the elastic band tool, and pass the tool through the foot as shown.  You should end up with one loop of elastic band passing over each fork-shaped end of the insertion tool.  The flat side of the tool should be on the outside, so that the channels in either end face towards the centre of the foot.  Make sure you pick the right foot - the middle axis (Z) has a smaller foot.  The angle of the feet is different, if the foot doesn't line up with the outside of the microscope casing, you may be using the wrong one.

You may find it easier to put the band through the foot, then insert the tool and hook the band over either end - either way you should end up with the band, foot, and tool arranged as shown in the pictures. The band tool holder can be placed on the short end of the band insertion tool to hold it at the correct angle and increase the area to push against.

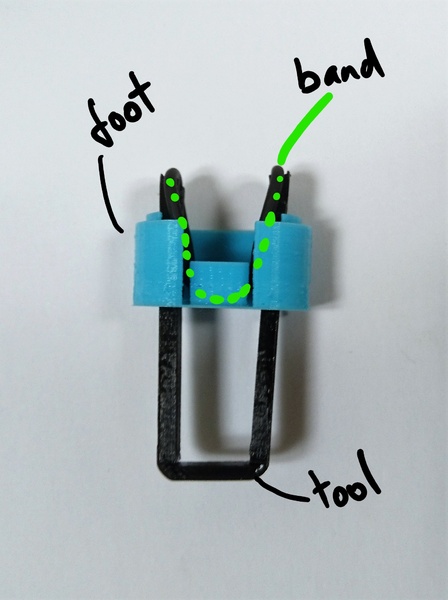
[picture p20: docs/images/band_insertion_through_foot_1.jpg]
The elastic band on the insertion tool, passed through the foot

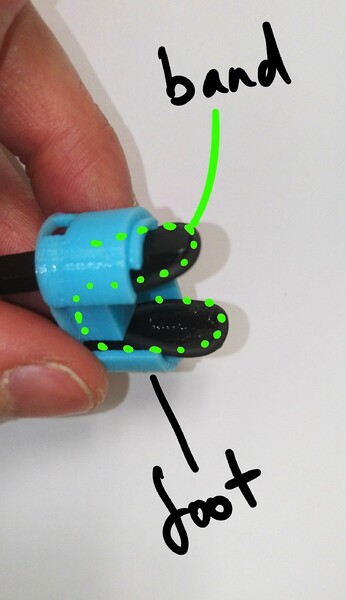
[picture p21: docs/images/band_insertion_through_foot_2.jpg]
Inserting the elastic bands


## Step 5
Place the foot on the body, taking care that it's in the right place (the outer two actuators have sloping bottoms, but flat tops, the central Z axis has a sloping top and a flat bottom). You must also take care to put them on the right way round; the open part of the foot points towards the optics module in the centre of the microscope.

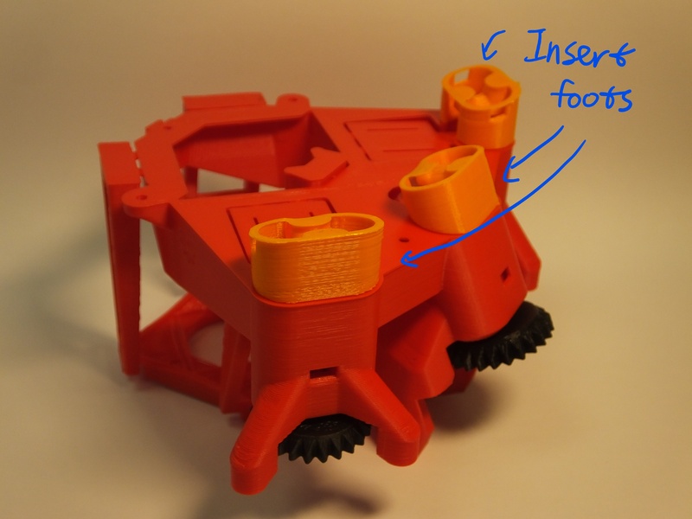
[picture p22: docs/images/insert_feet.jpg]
Feet fitted into the microscope

 
Push the insertion tool in until the band clicks into place.  Use the nut insertion tool to hold the actuator in place while you do this.  It might help to unscrew the gear a bit (so you can see some of the screw thread between the body and the gear) and push down on the gear.  When you push the band in, it should click twice - once for each side.  If you don't manage to hook both sides on, you may need to completely remove the band and try again - a wooden skewer, or small flat-bladed screwdriver works well to unhook the band without damaging it.
 
What's happening here is that the elastic band is pushed over little hooks inside the actuator column, near the top, and the click is the band popping into place.  The band pulls down on the actuator, so after it's in place the gear should turn with a little more resistance - this is important for the microscope to work properly.

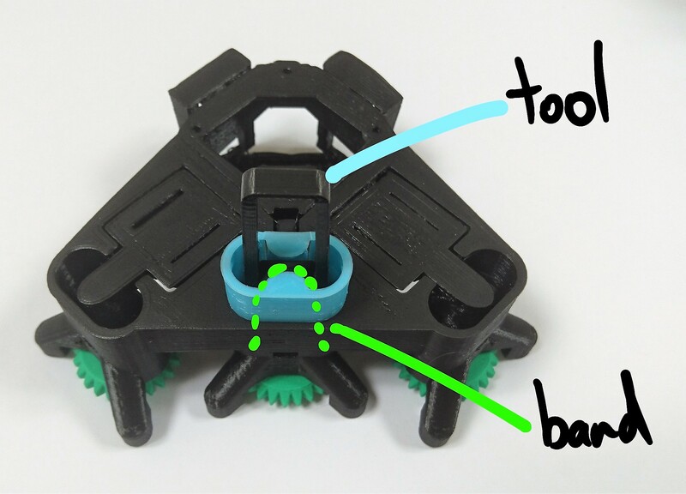
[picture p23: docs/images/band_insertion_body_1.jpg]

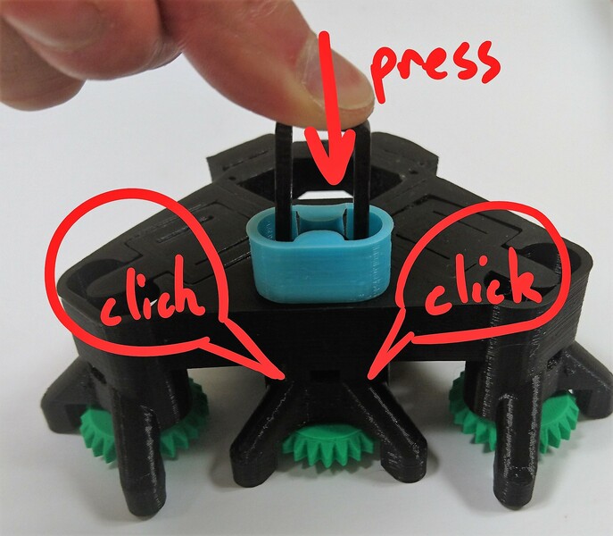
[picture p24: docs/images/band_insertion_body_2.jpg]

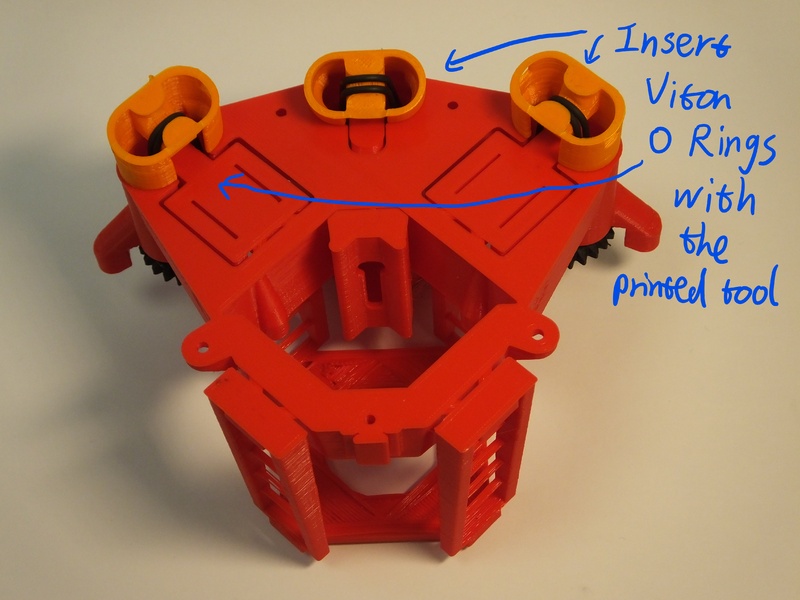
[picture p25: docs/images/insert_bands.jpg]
The bands and feet in place in the microscope body


## Step 6
You should now have the band pulling both sides of the actuator down as shown.
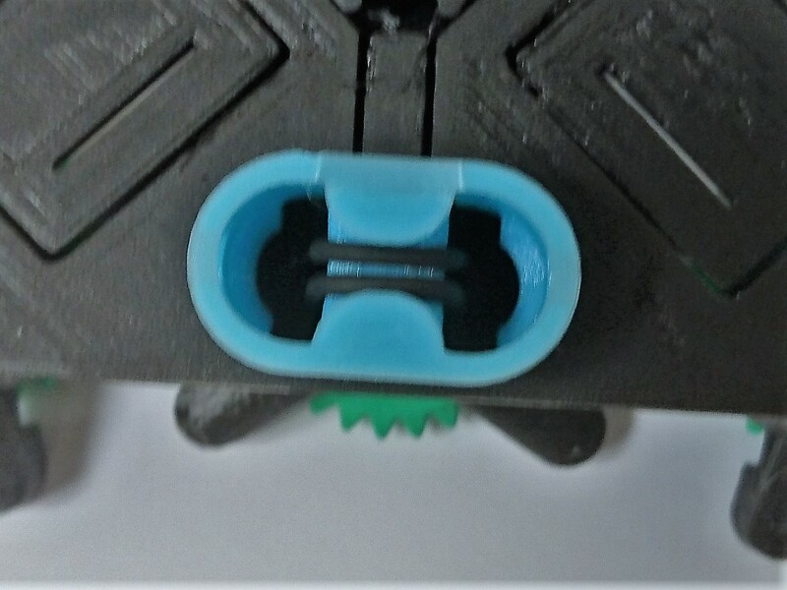
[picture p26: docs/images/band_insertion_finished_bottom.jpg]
The Viton o ring, in place in the microscope's foot.


## Step 7
Congratulations, you've assembled the actuator!  There are three to do, so you may now need to go back and make the next one.

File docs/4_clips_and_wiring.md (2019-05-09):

# Sample mounting and wiring

# Requirements
All the parts you need are shown below:

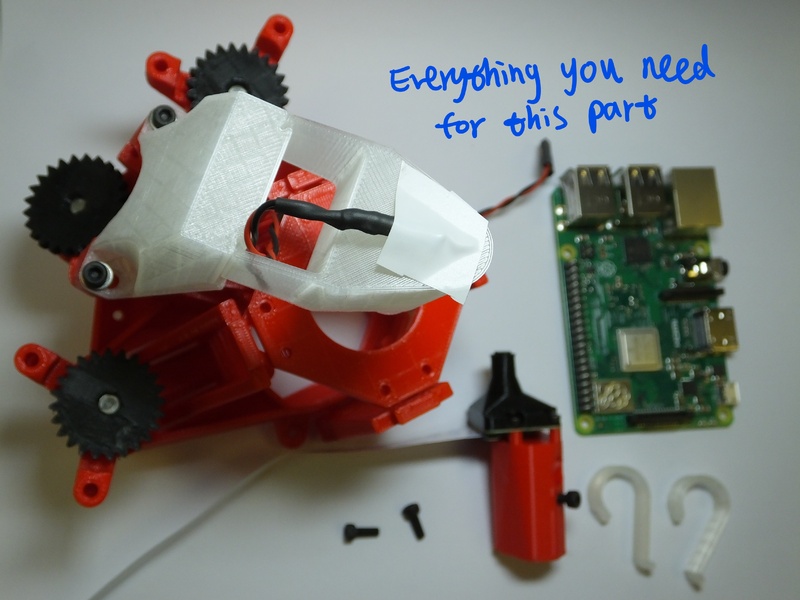
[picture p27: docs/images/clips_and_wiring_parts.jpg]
Parts needed for this section


## Parts
*   1 Microscope body, with 3 assembled actuators, an optics module, and the illumination attached.
*   2 [M3x8mm cap head screws](./parts/fixings/m3x8mm_caphead_screw.md) 
*   [Sample clips](./parts/printed/sample_clips.md)
*   [Raspberry Pi](./parts/electronics/raspberry_pi.md)

## Tools
*   A 2.5mm ball-ended hex key

# Assembly Instructions
## Step 1
Plug the LED cable into the GPIO connector on the Raspberry Pi, to the 0v and 5v lines.  These are the second and third pins from the top of the connector, on the outside edge - pins number 4 and 6.

Plug in the camera to the camera connector as described in the [Raspberry Pi learning materials](https://projects.raspberrypi.org/en/projects/getting-started-with-picamera) (the connector is next to the Ethernet port, and the contacts on the cable face the port, i.e. they face away from the tab on the plug).
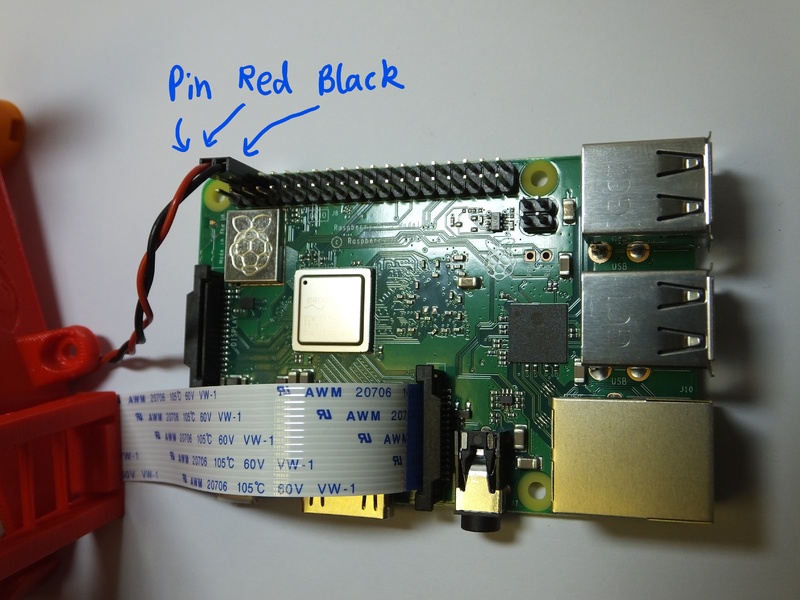
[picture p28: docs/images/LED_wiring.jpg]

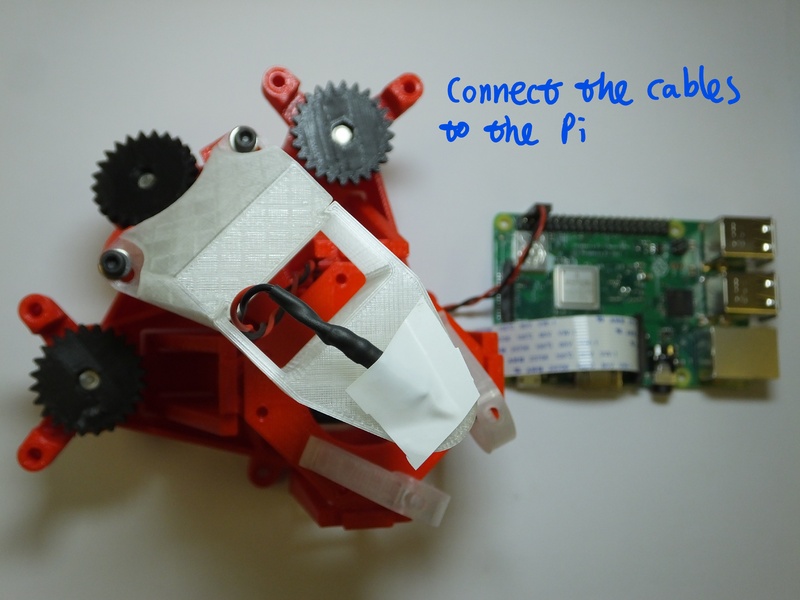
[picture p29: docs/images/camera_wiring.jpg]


## Step 2
If you are using a tall optics module, e.g. if you are using a plan corrected objective, you may need to fit a [sample riser](./parts/printed/sample_riser.md) between the microscope body and the microscope slide.  This is not necessary if you are using the basic optics module.

## Step 3
Fit the optics module onto the microscope - it slides in from the bottom as shown.  The screw sticking out the side fits into the "keyhole" shaped slot in the microscope body.
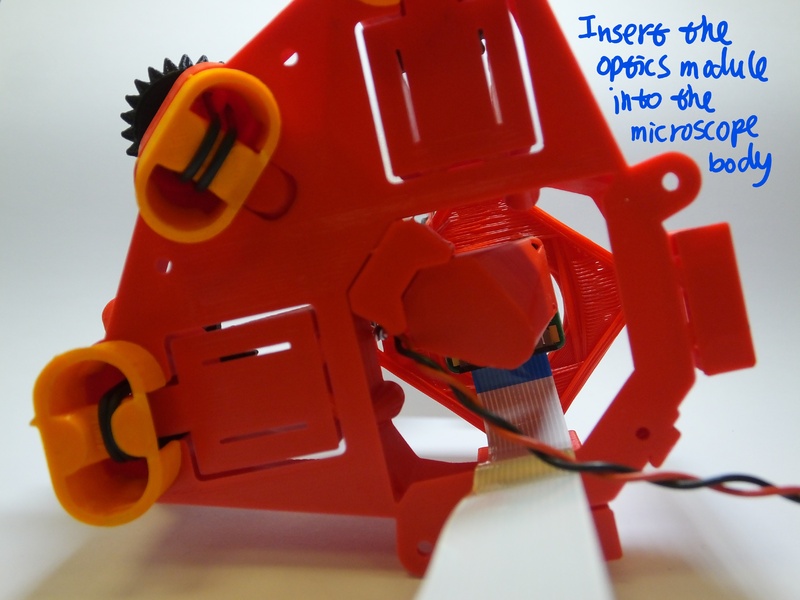
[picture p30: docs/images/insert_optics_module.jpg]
Insert the optics module


## Step 4
Tighten the screw to hold the optics module in place.  You can reach the screw with a ball-ended hex key, through the hole near the Z axis, as shown below:
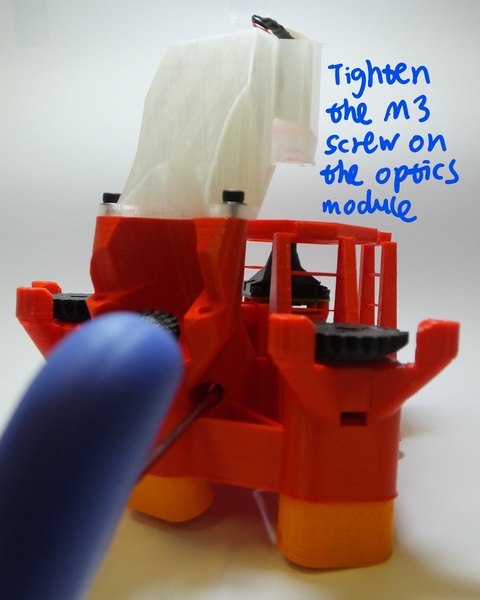
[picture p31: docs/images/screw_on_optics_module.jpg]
Tighten the screw to secure the optics module


## Step 3
After this, there are only the sample clips to go.  Exactly where you place these will depend on the samples you intend to use, but in any case you simply push the M3 screws into the clips, then screw down into the holes on the stage.
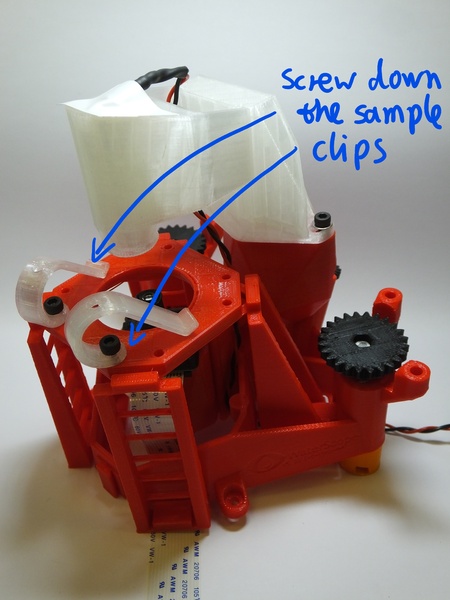
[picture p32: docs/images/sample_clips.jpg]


## Step 4
Your microscope is now complete - happy observing!
You might want to consult the [camera module documentation](http://www.raspberrypi.org/documentation/usage/camera/) or [raspicam documentation](http://www.raspberrypi.org/documentation/usage/camera/raspicam/README.md) if you need a hand setting up the camera.
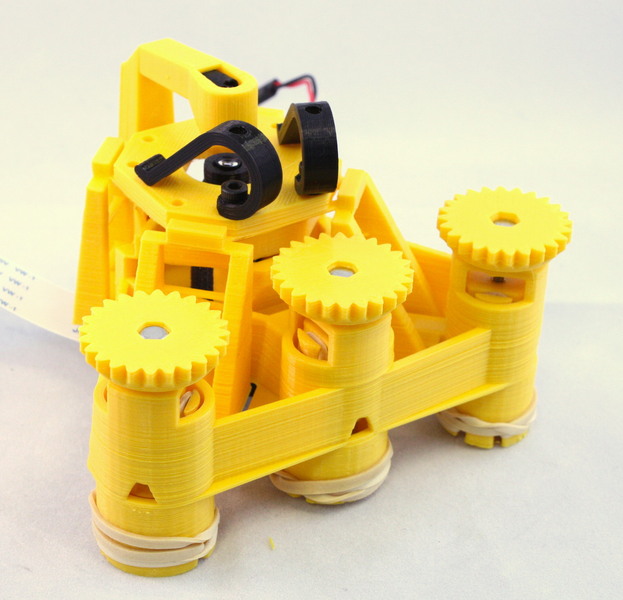
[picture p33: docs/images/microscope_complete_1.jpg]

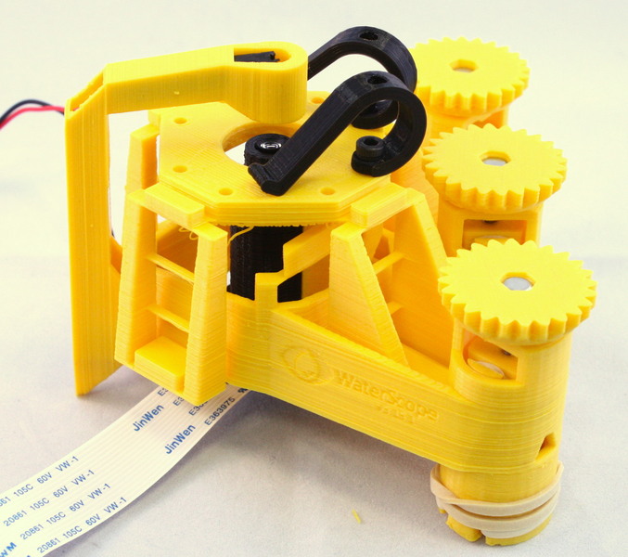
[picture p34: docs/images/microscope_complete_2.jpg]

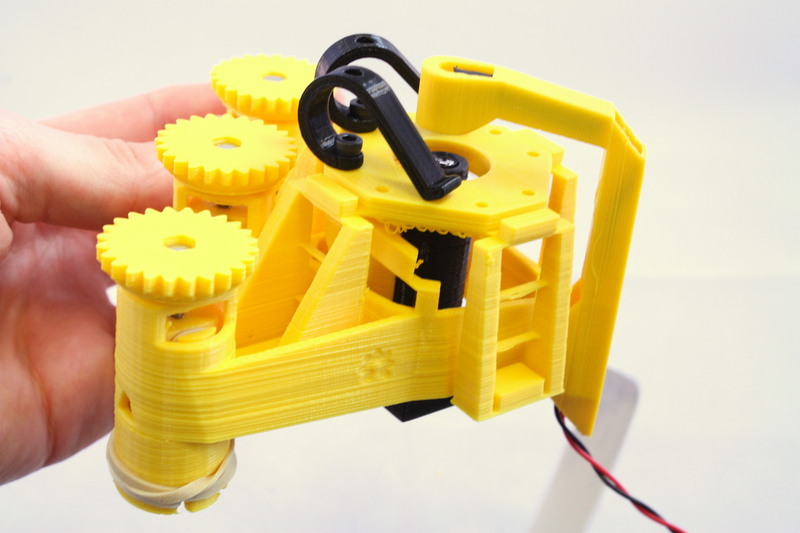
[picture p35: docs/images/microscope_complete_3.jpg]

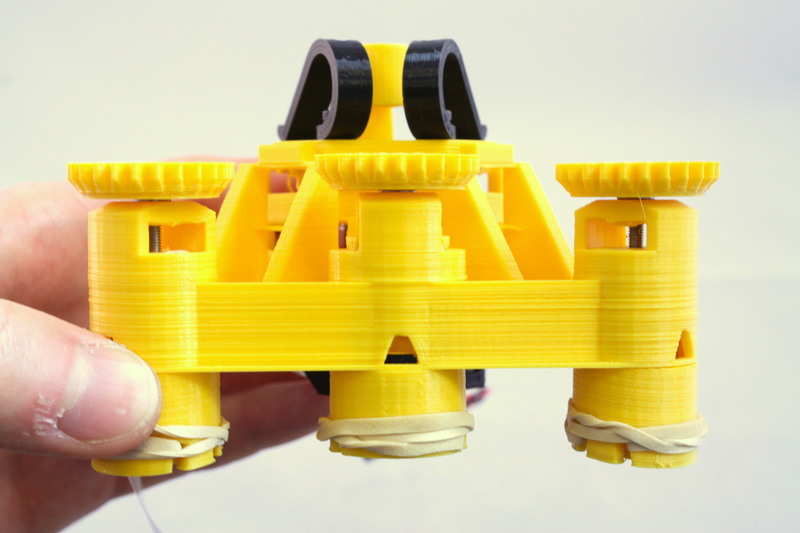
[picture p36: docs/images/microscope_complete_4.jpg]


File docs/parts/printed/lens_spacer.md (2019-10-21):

# Lens Spacer
This part mounts the lens to the camera board, inverted and spaced away from the sensor, and is the counterpart to the [camera platform](./camera_platform.md).  If you are using the lens that came with your webcam, you should probably use this option for the optics module - the one-piece [optics module casing](./optics_module_casing.md) replaces this part if you are building a high resolution microscope.

## STL File
The STL file for this part is called ``lens_spacer_<camera>_<lens>_LS65.stl`` where ``<camera>`` is currently only ``picamera_2`` and ``<lens>`` is currently only ``pilens``.  An alternative version for an M12 lens and the 6-LED webcam is available from STICLab.  This allows it to be used with either the $3 6-LED webcams favoured by various low-cost instruments, or the Raspberry Pi camera module.

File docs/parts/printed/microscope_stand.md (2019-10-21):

# Microscope Stand
The stand will hold the microscope flat on a table, and can also house a Raspberry Pi computer to control the microscope.  It can optionally stack on top of the [motor driver case](./motor_driver_case.md) if you need to mount a motor controller.

## STL Files
There are three versions:
* ``microscope_stand_30.stl`` holds a Raspberry Pi.
* ``microscope_stand_30-BS.stl`` holds a Raspberry Pi and supports the [reflection illuminator](./reflection_illuminator.md).
* ``microscope_stand_no_pi`` is less tall, and doesn't hold the Pi.

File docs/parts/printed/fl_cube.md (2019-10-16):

# Reflection/fluorescence cube

The filter cube allows for reflection illumination, by inserting a 50/50 beamsplitter filter into the 45 degree slot. It also enables fluorescence microscope, by instead inserting a dichroic filter in the 45 degree slot, and a long-pass filter in the bottom slot.

The cube is provided in a single file ``fl_cube.stl``.

Note, this must be used in conjunction with the [reflection illuminator](./reflection_illuminator.md).

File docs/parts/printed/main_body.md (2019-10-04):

# Microscope Body
This part is the main body of the microscope, including all the flexure mechanisms.  It's by far the biggest print, and is where most of the exciting bits live.

## Printing Instructions
This should be printed without support material.  On smaller/less well calibrated machines, I print this part on its own and then print the rest of the parts in a second print.  Which version of the body you need depends on two things: firstly, the height of the stage, and secondly whether you want attachment lugs for motors.  The microscope body takes around 10 hours on a RepRapPro Ormerod (and many other low-end printers) or about 8 hours on Ultimaker, MakerBot, or Prusa i3 Mk3 and the like. 

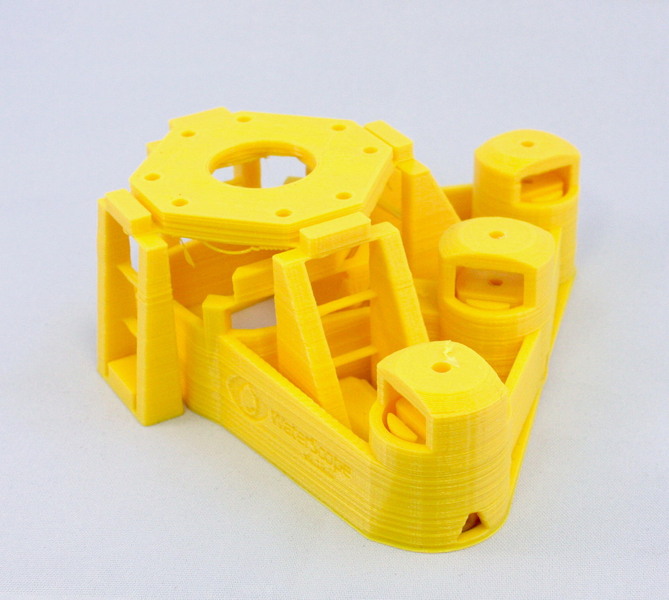
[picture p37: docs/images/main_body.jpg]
A picture of the main body


### STL File
The main body is printed from ``main_body_LS<height>.stl``, or ``main_body_LS<height>-M.stl`` where ``<height>`` is either 65 or 75 depending on how tall you want the microscope to be.  We almost exclusively use a height of 65mm, and if a taller stage is required (e.g. to use a larger microscope objective) we combine it with a [sample riser](./sample_riser.md).  The ``-M`` in the filename means it includes motor lugs - these allow you to attach stepper motors to the microscope and move it automatically.  If in doubt, print ``main_body_LS65-M.stl`` because you can always just ignore the lugs, and add a riser, if it turns out you have the wrong one!

### Actuator cleanup
After printing, you may run a 3mm drill bit through the 3mm holes in each actuator, to ensure the screws can rotate freely (usually this is not necessary).
drilling out the hole for the actuator

### Brim cleanup
If the bottom layer has oozed out too much, or if you used a brim you might need to clean up the bottom so it looks like this - it's important that the moving parts aren't stuck to the body with a thin layer of plastic.
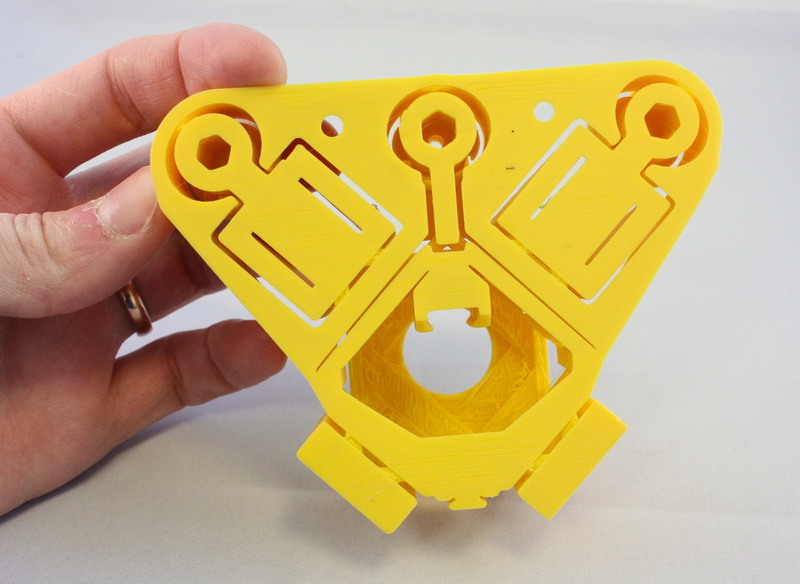
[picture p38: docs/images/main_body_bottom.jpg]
The bottom of the microscope body


### Cleaning up the bridges
You may need to use needle-nose pliers to pull strings of plastic from the underside of the microscope stage.  If your printer is correctly calibrated there shouldn't be much, and I often get away without any - but some printers (particularly if using ABS) are prone to a bit of "spaghetti" under the stage.

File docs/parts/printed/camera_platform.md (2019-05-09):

# Camera Platform
This part mounts the camera onto the body of the microscope, and is the counterpart to the [lens spacer](./lens_spacer.md).  If you are using the lens that came with your webcam, you should probably use this option for the optics module - the one-piece [optics module casing](./optics_module_casing.md) replaces this part if you are building a high resolution microscope.

## STL File
The STL file for this part is called ``camera_platform_<camera>_LS65.stl`` where ``<camera>`` is currently either ``6led`` or ``picamera_2``.  This allows it to be used with either the $3 6-LED webcams favoured by various low-cost instruments, or the Raspberry Pi camera module.

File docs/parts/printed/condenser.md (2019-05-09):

# Condenser arm
This part holds the condenser lens and LED, for transmission illumination.  It can be printed from ``condenser.stl``.

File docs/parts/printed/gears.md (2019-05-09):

# Large Gears
These gears are used to control the leadscrews that move the stage.  You can replace them with more comfortable thumbscrews if desired, or use stepper motors to drive them automatically.  You need three gears, and ``gears.stl`` contains all three (they are identical).  NB the gears are designed to print with the circular face down, this avoids marring of the teeth and helps it stick to the bed better.

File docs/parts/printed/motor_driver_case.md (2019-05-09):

# Motor driver case
If you are controlling the microscope with motors, this "bucket" fits underneath the [microscope stand](./microscope_stand.md) and holds the [control electronics](../electronics/motor_driver.md) - usually a Sangaboard.

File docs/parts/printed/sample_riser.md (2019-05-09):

# Sample Riser
This is a spacer that fits between the stage and the microscope slide, to raise it up.  It is mostly useful for fitting a 45mm parfocal objective into the LS65 microscope body.

## STL File
* ``sample_riser_LS10.stl``
The number following ``LS`` is the thickness of the riser in millimetres.

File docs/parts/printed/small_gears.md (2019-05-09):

# Small gears
If you fit motors to the microscope, the motors need small gears on them to mesh with the large [gears](./gears.md) that control the microscope.  You need three gears, and the STL file provides all 3.  NB the gears have a flat lip around the bottom - this is to help them stick to the print bed and avoid the teeth being distorted, so it should be at the bottom when printed.

## STL File
* ``small_gears.stl``

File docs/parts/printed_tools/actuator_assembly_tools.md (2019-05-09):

# Actuator assembly tools
This printable file includes both the nut insertion tool (the short one) and the elastic band insertion tool (the longer tool, that folds into a U shape).  It should be oriented correctly for printing - hopefully the flat bottom is fairly obvious.

## STL File
* ``actuator_assembly_tools.stl``

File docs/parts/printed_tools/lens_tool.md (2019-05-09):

# Lens insertion tool
This printed tool will push a lens into the plastic housing, touching only the edge of the lens.  This minimises damage to the lens, and ensures it is firmly pushed in.

## STL File
Print ``lens_tool.stl``.

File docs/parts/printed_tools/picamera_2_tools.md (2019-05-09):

# Raspberry Pi Camera lens removal tools
These tools make it easier and safer to remove the lens from a Raspberry Pi camera module.  See the documentation for the optics module for instructions.  These tools are for version 2 of the camera board, if you have a v1 camera module you may need to use mini pliers to remove the lens.  Version 2 of the Raspberry Pi camera module now comes with a lens removal tool, which is better than the printed one - but the board gripper is still useful.

## STL Files
There are two printable tools that are useful:
* ``picamera_2_gripper.stl`` is a rectangular jig that fits over the board, and stops the camera module from twisting when you unscrew the lens.
* ``picamera_2_lens_gripper.stl`` is a "spanner" to unscrew the lens.  Use this only if you don't have the original white plastic tool that is supplied with the camera module.

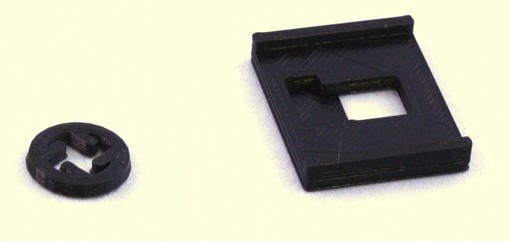
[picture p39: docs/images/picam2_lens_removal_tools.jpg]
The lens removal tools


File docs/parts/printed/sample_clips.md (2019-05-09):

# Sample Clips
These are optional, but they are useful for holding slides on the stage.  Usually, I use two of these for a normal microscope slide, screwed onto the top of the stage.

## STL File
*   ``sample_clip.stl``

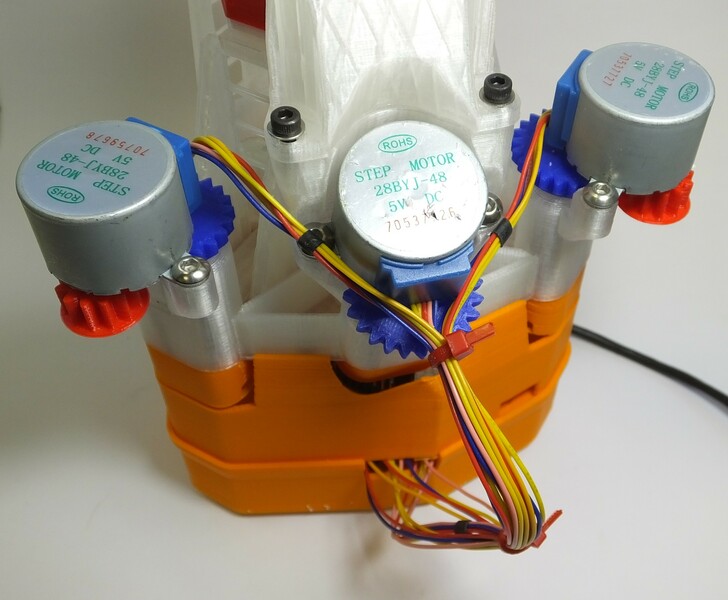
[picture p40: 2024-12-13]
docs/images/motors_assembled.jpg

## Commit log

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2016-03-23 Removed illumination column and replaced with dovetail
    Former-commit-id: c02a423c66db3ad651070986fbe575c370febaa9
    [dovetail.scad, illumination_and_rear_foot.scad, main_body.scad]
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2016-04-06 Unified RMS and picam models
    Everything now compiles from the same (slightly monster) file. Probably
    need to fix the tube lens placement though.
    Former-commit-id: aa8002664ddd4d7af214e4129d86ddbd81f68721
    [optics_all_in_one.scad]
2016-04-06 Fixed RMS tube lens position and consolidated everything.
    Former-commit-id: c2422411f82baff1ebe9bf0b772586668ebb5e26
    [RMS_camera_mount.scad, optics.scad, optics_all_in_one_6mm_achromat.scad, optics_all_in_one_6mm_achromat_2.scad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]
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2016-04-19 Redesigned illumination to fit with dovetail the other way around.
    Former-commit-id: eac3925bd6cc449da0c13852f03ff35ef307727d
    [dovetail.scad, illumination_and_rear_foot.scad, main_body.scad]
2016-04-23 Improved dovetail and illumination
    It’s now got an endstop, and it’s thick where it needs to be but not
    everywhere else (prints faster and more clearance for cables).
    Former-commit-id: 395e9228b7fd7ce0adda585343ae2613e9b15047
    [dovetail.scad, illumination_and_rear_foot.scad]
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2016-05-05 Fixed slash in include
    forward slash it turns out is platform-independent. Backslash confuses
    mac/linux machines.
    Former-commit-id: e015672225f98325910edc281e552c1996f2a638 [formerly 05a242d73431d6de293ac923d439495c592b0833]
    Former-commit-id: f4411b10f7199cf07e64bbc09a2e3eb7a88aec42
    [gears.scad]
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2016-06-20 Joined legs correctly onto main body.
    The bottom flexures weren’t actually part of the main body - there was
    a zero width gap between the flexures and the wall. This is now fixed.
    Also, I added slight indents either side of where the flexures join the
    wall to ensure it’s properly retained.
    Former-commit-id: b82c1bb478412e072f6729fc3af93684c1b0a0ef [formerly b806cc6d23d401ee3f252cd37a1a0129833a3464]
    Former-commit-id: 6cf6d0412e323c1b5eb5536785cefa141dfe9f23
    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
    [main_body.scad, microscope_parameters.scad]
2016-06-21 Another fix to the attachment of legs to body
    The sloping-in wall round the microscope body meant the flexures
    weren’t attaching (on some printers/slicers) - I’ve now made them go
    further in to the body, so they connect properly.
    Former-commit-id: 7585eca2f42765c279153ac2d8223c8b399ff39b [formerly 45449058d6155b34640e9bdf09945926d4dc6ec1]
    Former-commit-id: c9ebfbf00f493803036593bb34ff99f14a5da4ef
    Former-commit-id: 7cee3519a61e65d1e64e1f79b763c640289619db
    [main_body.scad]
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2016-09-26 Thinned the bottom of the objective clip dovetail
    I'd inadvertently added 0.5+d to the thickness of the dovetail clip for
    the objective. That made it hard to clip in, and caused trouble when it
    broke, as it often did. The new, thinner bottom should be stretchier
    and easier to snip off if desired. Need to recompile the STL
    Former-commit-id: d24e4cb2d818f6d2939ec7c31072d783ede38d02 [formerly 08bdb968db6f8ca238cc5b7fff314c61c924a456]
    Former-commit-id: 92791c45440b9167f8f45c9cfe4e8433fdeda35e
    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
    [main_body.scad]
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2016-10-28 variable led_r went nowhere, fixed
    at the top of the file, the variable led_r did not, as labeled, change
    the diameter of the LED holder. Also, while labeled ‘r’ it actually
    required a diameter-based input.
    I changed the variable to led_d and inserted it into the equations on
    lines 93 and 94.
    Former-commit-id: cedd3aa709b7bba48145f8515a480a8d6b18a5cd [formerly 8e11f01e634dad1a4ceefe077ebe4a0fdc0accfb]
    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
    [illumination_and_rear_foot.scad]
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2016-12-12 added shift parameter to move around the condenser
    With everything in the "perfect" position, the condenser seemed to be
    about 2mm too far towards the Z nut. I've shifted it back, but I'm
    worried that's a tolerance issue rather than a static shift...
    Former-commit-id: 868f3dd5f9a8b008b756a6e4e2d285765effb4f4 [formerly 1cf1d4dc79fd138f2949d67c97ce738503dbe5f8]
    Former-commit-id: 1c5df89f3ba7a539a67ef4ea0a99c280c1e4798e
    Former-commit-id: db92ff87a11991da942a959014e2c9901485cc24
    [illumination_and_rear_foot.scad]
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2017-01-16 Rebuilt vanilla body to fix leg attachment issue
    Former-commit-id: 45d87aad449ad2417da1f77d54cce58e86e84f63 [formerly ee410de1383cff0495a4f6a800d94a9e5bd57f55]
    Former-commit-id: 6e612b3fd4fe2ea7907f26e28fb3adb5ab4b4c54
    Former-commit-id: b9b645e1986d6a9aa42f01cb0ac9dfdf49fa100a
    [microscope_parameters.scad]
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2017-02-08 tightened nut trap and strengthened hooks
    Tweaks to geometry of the actuator column, to make the nut fit more
    snugly and make the hooks for elastic bands stronger.
    Former-commit-id: da4d6768d71b69eafdb9a40eb18937f1cdc6423a [formerly 6c63c5a0a5d145cd336bb44c96eeff0c0397e1a3]
    Former-commit-id: a3260e6abb694238206a0230ae0937caa5b7c403
    Former-commit-id: fc8ac84aad8501ee48b31f2cf9d961f16f15f450
    [compact_nut_seat.scad]
2017-02-08 Bug fix and trylinder gripper for pi lens optics
    Added a new (untested) optics module for the pi lens, using a
    "trylinder" gripper to avoid tape. Also fixed a bug introduced by
    fluorescence that caused non-fluorescence optics modules to fail.
    Former-commit-id: 62ef777d8674c8e84c9a33fb88444db86b775239 [formerly b6a083d6d30f0d70e9d132ca2b903fccd846c9b9]
    Former-commit-id: 88afaa01adc72cd1578eb63c7018fcab0a40ff04
    Former-commit-id: 3932bf2c73188e11f6544e0504c233188a21563f
    [optics.scad]
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2017-02-08 Fixed issues with feet
    The bottom of the feet is a simple shape - an oval outline with a
    section filled in in the middle. This should have a break for the
    elastic band, but it's missing on the tilted feet; I've now fixed this.
    Former-commit-id: d5f3525f3b908b502e93f2fde98bd2ad5ff12c69 [formerly e9bb98e7689cc5884404060d0bff946c0df4a5e8]
    Former-commit-id: d922ae0ede531d78ce5f6e416c55d2dba826d690
    Former-commit-id: 25499ea1cceac2ab862c887e448617b022a8f866
    [compact_nut_seat.scad, feet.scad, microscope_parameters.scad]
2017-02-09 Fixed feet
    By introducing nut_w I screwed up the feet... now fixed.
    Former-commit-id: 31df02edcd056d698b076aaa31391973334b3033 [formerly 622d3d62f26148c2f3cd8cdec2ae868a63222570]
    Former-commit-id: fffcf05a801c868fbcbebd5c16be6f8781988d1c
    Former-commit-id: 80a81f350c199baaab5d9d51d0cf93b5bc267b06
    [compact_nut_seat.scad, feet.scad, utilities.scad]
2017-02-09 Tightened nut slots a bit more
    Former-commit-id: 57a2fc0eb33a9142832efcef0d32b0b793ebe8b7 [formerly 8e671b34a38159781f08c38770e020861c4b297e]
    Former-commit-id: 84f62746229a2a95e3af739e2119e0fda5c2efe2
    Former-commit-id: 4562173769f231b9c36766751416c4a54cf41030
    [compact_nut_seat.scad, microscope_parameters.scad]
2017-02-10 Tightened nut seat and recompiled
    it's too tight now!!
    Former-commit-id: ad2b2737adf611cb7de8c97f0d5561da9d160f66 [formerly ad594d5b8e845c7cd4359b767962af2a01ac68c6]
    Former-commit-id: c37b488658541c4e99998f516f306b4f80ae19cf
    Former-commit-id: c6400e814a49894a6548e69c293e133320298fc8
    [compact_nut_seat.scad, gears.scad, microscope_parameters.scad]
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2017-02-17 fixed some bugs in the wall
    Former-commit-id: a9ba72a70868c585c56339fa1e7e34f8d24a991d [formerly 95d0e73432523d15a3f898cacf0db8e698742731]
    Former-commit-id: ec882b0e108fc49edb23fd466de2991ebe28b022
    Former-commit-id: 184e5fa91c6911f747846bc7f8ac2cc4b80abfb8
    [compact_nut_seat.scad, main_body.scad, microscope_parameters.scad]
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2017-02-22 Fixed the screw shaft so it's long enough.
    I previously shortened the screw shaft inside the column - unfortunately
    I shortened it too much. I've now made it longer, but tapered the end
    for strength. The STL files are not updated so I deleted them.
    Former-commit-id: 12995df74aadff23e745c3e8844cf8361214c802 [formerly c3ab202e25948c0f651b23e292d420d53c913efd]
    Former-commit-id: f5ba81cda03ae38a37c4805cacac115ea976a97c
    Former-commit-id: d319792ec0ee549b166eb8d5689dc0d298092c73
    [compact_nut_seat.scad]
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2017-03-01 Loosened the fit of the assembly tools
    Former-commit-id: cfff9084ddb6ede93e45c52bbe18caa378a31bff [formerly c4c213fdee5c7661f933028bf69b76cc6fa7e597]
    Former-commit-id: da4ca7b91024a85482f9f8d7d2d7ff28b5e2a466
    Former-commit-id: 2473d79549a33f011c3bbd8ee70832a68bf7a3e6
    [actuator_assembly_tools.scad]
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2017-03-02 Fixed a bug that broke the stage legs
    The flexure bridges that support the stage were failing - turns out I
    hadn't quite joined them on properly. This is now fixed.
    Former-commit-id: 47d1beb61600712b8a23488d46725450762a8659 [formerly 3062b2917b924aff4c4ce79417ec6895c5c260e6]
    Former-commit-id: 03242e5ebdcf44cfff76b2ffaa6c718b0ce4fa6a
    Former-commit-id: da10936c678c01f23d0dc3523dd5720371a6d399
    [main_body.scad, microscope_parameters.scad]
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
